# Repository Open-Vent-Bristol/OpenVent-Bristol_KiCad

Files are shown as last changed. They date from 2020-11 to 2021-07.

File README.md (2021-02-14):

OpenVent controller PCB, version A (KiCad) ported from version 2.7 (Altium,
incomplete), 2020-10-20, by Jeff Sutherland <jeffs@fomsystems.com>

All files for the Power Board are in the subfolder called "OV_Power". All control/main board files are in this folder level.
Electronic system diagram and overall device system diagram can be found here: https://docs.google.com/presentation/d/e/2PACX-1vRULcGT6Jc9GJDVb21LnrkGW9OiDjC7QJ2lRb0DsiA6KYFimniAMwYWqoMfq-0fJhvekxmhCl915fU4/pub?start=false&loop=true&delayms=3000&slide=id.gb10047446c_0_106
Also found by clicking "build" on https://openventbristol.co.uk/

Altium conversions aren't perfect but most everything is here.  Because the
schematic was incomplete and would not pass validation in Altium due to not
being complete a few things didn't make it across symbol-wise.  These will
have to be re-created in KiCad, but this is a trivial exercise.  Of more
import is the assigning of properties to all of the symbols in the schematics
so a sensible Bill of Materials may be generated directly from the schematic
or finished PCB layout.

All of the footprints that were currently in the Altium PCB came over and are
stored in the project footprint library.  These do not necessarily match the
schematic since the Altium PCB design reflects a former version of the
schematic as it had not been updated as yet.  So there is still much to do
before we can begin the process of creating the layout.  New mechanical
information is needed (see project documents).  The PCB layout for the former
version, stored for reference in the file "OpenVent_PCB-PcbDoc.kicad_pcb" does
not reflect the correct mechanical outline nor placement of components.  The
PCB footprints from the Altium design are missing information needed by KiCad
so if replacements are not available in the standard KiCad libraries then
these will have to be fixed.

TO DO's:
Complete schematic:
  a. Add BOM info to all symbols
  b. Complete circuit design
  c. Validate design

Process Board layout:
  a. load in missing footprints (use KiCad libraries, avoid creating
     footprints by hand if at all possible, if needed, fix existing ones.)
  b. Update PCB board outline, mech drill holes, and update placement and
     routing keepout areas
  c. Complete board placement and routing.
  d. Check association of footprints and 3D bodies; prepare STEP file of 3D
     image of board for mechanical group.

When creating symbols or updating fields in the schematic use the following
patterns for adding information to symbols in the lib or schemo:
   
   Field 0 is always 'Reference'
   Field 1 is always 'Value'
   Field 2 is always 'Footprint'
   Field 3 is always 'Datasheet'

These cannot be changed as they are required by the system.  The remaining
fields can be freely defined.  So in the case of OpenVent we need to
standardize how these are used to make sensible BOM generation possible.  For
example, something like this scheme could be used:

   Field 4 is defined as 'Val' (resistance, capacitance, inductance, etc.)
   Field 5 is defined as 'Voltage'
   Field 6 is defined as 'Tolerance'
   Field 7 is defined as 'Watt'  (usually just for resistors)
   Field 8 is defined as 'Current'  (usually for diodes and inductors)
   Field 9 is defined as 'Mfr' (manufacturer name)
   Field 10 is defined as 'Mfr_PN' (manufacturer's part number)
   Field 11 is defined as 'DistName' (this would be Farnell, DigiKey, etc.)
   Field 12 is defined as 'Dist_PN' (distributor's part number)
   Field 13 is defined as 'Detailed' (detailed description of part)

Optional fields can be added at will in the schematic to suit the needs of the
design or documentation efforts.

Notes on using KiCad:

  1. When setting up your KiCad installation you should also clone the
     repositories for the symbols, footprints and 3D models and refer to those
     in your 'manage libraries' settings rather than using the default
     libraries that came with your version of KiCad.  See github.com/kicad.

  2. Do not just add symbols to the design from the KiCad standard libraries.
     The symbols there are basically just "templates".  Copy standard symbols
     to a project library then add BOM and footprint info to the symbols if
     needed.

  3. Avoid creating your own footprints if at all possible.  Most every IC in
     common use already has a standard footprint in the KiCad libraries.

  4. All footprints should be kept in a local project library.  If
     modifications need to be made to paste or solder mask layers to deal with
     process issues copy footprints to another library and tag that library with
     the name of the PCB vendor so that managing artwork fudging among vendors can
     be easily sorted.

     After footprints are pulled into the PCB design from the standard KiCad
     libraries they may be exported to a local library to facilitate modifying any
     of their shapes to meet DFM requirements of a particular vendor.  Simply
     export the footprints to a project library from the PCB editor once the
     design has been transferred from the schematic and all the footprints
     have been accounted for.  There's no need to manually copy footprints
     from the KiCad libraries.

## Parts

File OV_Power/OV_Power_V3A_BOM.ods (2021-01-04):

Reference | Value | Footprint | Datasheet | Current | Desc | Detailed | DistName | Dist_PN | Mfr | Mfr_PN | Voltage | Tolerance | Val | Watt | Tol | Volt | DK_pn | Colour
Q2 | 2N7002BK | Package_TO_SOT_SMD:SOT-23 | https://assets.nexperia.com/documents/data-sheet/2N7002BK.pdf | 350mA | MOSFET N-CH 60V 350MA SOT23 | N-Channel 350mA (Ta) 370mW (Ta) Surface Mount TO-236AB | DigiKey | 1727-4789-2-ND | Nexperia USA Inc. | 2N7002BK,215 | 60V
C9 | 1uF_0603_Ceramic_Capacitor,_10%,_50V,_X5R | Capacitor_SMD:C_0603_1608Metric |  |  |  |  |  |  |  |  | 50V | 10% | 1uF
C1 | 100nF_0603_Ceramic_Capacitor,_10%,_X7R,_25V | Capacitor_SMD:C_0603_1608Metric |  |  |  |  |  |  |  |  | 25V | 10% | 100nF
U1 | LT3796 | F_ICs:TSSOP-28-LTvar_EB_4.4x9.7mm_P0.65mm | http://www.analog.com/media/en/technical-documentation/data-sheets/3796fb.pdf |  | IC LED DRIVER CTRLR DIM 28TSSOP | LED Driver IC 1 Output DC DC Controller SEPIC, Step-Down (Buck), Step-Up (Boost) Analog, PWM Dimming 28-TSSOP-EP |  |  | Analog Devices | LT3796IFE-1#TRPBF
L1 | MSD1260-333 | F_Inductors:MSD1260 | https://www.mouser.com/datasheet/2/597/msd1260-220355.pdf |  | Coupled Inductors 33uH | Coupled Inductors 33uH Shld 20% 2.32A 134mOhms | Mouser | 994-MSD1260-333MLB | Coilcraft | MSD1260-333MLB |  |  | 33uH
R10 | R_0805_050m_cursense | Resistor_SMD:R_0805_2012Metric | https://www.ohmite.com/assets/docs/res_kdv.pdf?r=false |  | RES 50M OHM 1% 1/4W 0805 | 50 mOhms ±1% 0.25W, 1/4W Chip Resistor 0805 (2012 Metric) Current Sense Metal Film | DigiKey | 273-KDV08FR050ETTR-ND | Ohmite | KDV08FR050ET |  | 1% | 0.05mOhm | 0.25W | 1.00%
Q1 | SSM3K341R | Package_TO_SOT_SMD:SOT-23 | https://toshiba.semicon-storage.com/info/docget.jsp?did=35714&prodName=SSM3K341R |  | MOSFET N-CH 60V 6A SOT-23F | N-Channel 60V 6A (Ta) 1.2W (Ta) Surface Mount SOT-23F | DigiKey | SSM3K341RLFTR-ND | Toshiba Semiconductor and Storage | SSM3K341R,LF
C6 | 2.2uF_2824_film_capacitor_10%_40V | F_Misc:CAPPC7360X380N | https://www.wima.de/wp-content/uploads/media/e_WIMA_SMD_PET.pdf |  | CAP FILM 2.2UF 10% 63VDC 2824 | 2.2µF Film Capacitor 40V 63V Polyester, Polyethylene Terephthalate (PET), Metallized 2824 (7260 Metric) |  |  | WIMA | SMDTC04220TB00KQ00 | 63V | 10% | 2.2uF
D3 | MBRS260T3G | Diode_SMD:D_SMB | https://www.onsemi.com/pub/Collateral/MBRS260T3-D.PDF | 2A | DIODE SCHOTTKY 60V 2A SMB | Diode Schottky 60V 2A Surface Mount SMB |  |  | ON Semiconductor | MBRS260T3G | 60V
R15 | R_1206_250m_cursense | Resistor_SMD:R_1206_3216Metric | https://www.yageo.com/upload/media/product/productsearch/datasheet/rchip/PYu-PT-Group_521_RoHS_L_2.pdf |  | RES 0.25 OHM 1% 1/2W 1206 | 250 mOhms ±1% 0.5W, 1/2W Chip Resistor 1206 (3216 Metric) Automotive AEC-Q200, Current Sense, Moisture Resistant Thick Film |  |  | Yageo | PT1206FR-7W0R25L |  | 1% | 250mOhm | 0.5W | 1.00%
R11 | R_0603_015m_cursense | Resistor_SMD:R_0603_1608Metric | https://www.ohmite.com/assets/docs/res_lvt.pdf?r=false |  | RES 0.015 OHM 1% 1/3W 0603 | 15 mOhms ±1% 0.333W, 1/3W Chip Resistor 0603 (1608 Metric) Current Sense Metal Element |  |  | Ohmite | LVT06R0150FER |  | 1% | 0.015mOhm | 1/3W | 1.00%
R9 | R_0603_2k_0.1W_1% | Resistor_SMD:R_0603_1608Metric |  |  |  |  |  |  |  |  |  | 1% | 2k | 0.1W
RT1 | R_Thermistor_0603_10K_NTC | Resistor_SMD:R_0603_1608Metric | https://www.vishay.com/docs/33008/nths.pdf |  | THERMISTOR NTC 10KOHM 3477K 0603 | NTC Thermistor 10k 0603 (1608 Metric) | DigiKey | 541-1107-2-ND | Vishay Dale | NTHS0603N02N1002JE |  | 5% | 10K
R17 | R_0603_30k1_0.1W_1% | Resistor_SMD:R_0603_1608Metric |  |  |  |  |  |  |  |  |  | 1% | 30k1 | 0.1W
R18 | R_0603_95k3_0.1W_1% | Resistor_SMD:R_0603_1608Metric |  |  |  |  |  |  |  |  |  | 1% | 95k3 | 0.1W
R19 | R_0603_10k2_0.1W_1% | Resistor_SMD:R_0603_1608Metric |  |  |  |  |  |  |  |  |  | 1% | 10k2 | 0.1W
R16 | R_0603_113k_0.1W_1% | Resistor_SMD:R_0603_1608Metric |  |  |  |  |  |  |  |  |  | 1% | 113k | 0.1W
R14 | R_0603_49k9_0.1W_1% | Resistor_SMD:R_0603_1608Metric |  |  |  |  |  |  |  |  |  | 1% | 49k9 | 0.1W
R6 | R_0603_499K_0.1W_1% | Resistor_SMD:R_0603_1608Metric |  |  |  |  |  |  |  |  |  | 1% | 499K | 0.1W
R7 | R_0603_97.6K_0.1W_1% | Resistor_SMD:R_0603_1608Metric |  |  |  |  |  |  |  |  |  | 1% | 97.6K | 0.1W
R1 | R_0603_806K_0.1W_1% | Resistor_SMD:R_0603_1608Metric |  |  |  |  |  |  |  |  |  | 1% | 806K | 0.1W
R2 | 20k_0603_Chip_Resistor,_1%,_0.1W | Resistor_SMD:R_0603_1608Metric |  |  |  |  |  |  |  |  |  | 1% | 20k | 1W
R5 | R_0603_19k6_0.1W_1% | Resistor_SMD:R_0603_1608Metric |  |  |  |  |  |  |  |  |  | 1% | 19k6 | 0.1W
R3 | R_0603_499R_0.1W_1% | Resistor_SMD:R_0603_1608Metric |  |  |  |  |  |  |  |  |  | 1% | 499 | 0.1W
C3 | 10nF_0603_Ceramic_Capacitor,_10%,_50V,_X7R- | Capacitor_SMD:C_0603_1608Metric |  |  |  |  |  |  |  |  | 50V | 10% | 10nF
R4 | R_0603_40k2K_0.1W_1% | Resistor_SMD:R_0603_1608Metric |  |  |  |  |  |  |  |  |  | 1% | 40k2 | 0.1W
C2 | 10nF_0603_Ceramic_Capacitor,_10%,_50V,_X7R- | Capacitor_SMD:C_0603_1608Metric |  |  |  |  |  |  |  |  | 50V | 10% | 10nF
C8 | C_1210_10uF_25V_10%_X7R | Capacitor_SMD:C_1210_3225Metric | http://www.samsungsem.com/kr/support/product-search/mlcc/CL32A106KAULNNE.jsp |  | CAP CER 10UF 25V X5R 1210 | 10µF ±10% 25V Ceramic Capacitor X5R 1210 (3225 Metric) |  |  | Samsung Electro-Mechanics | CL32A106KAULNNE | 25V | 10% | 10uF
U2 | LT1936 | F_ICs:LT_MS8E | https://www.analog.com/media/en/technical-documentation/data-sheets/1936fd.pdf |  | IC REG BUCK ADJ 1.4A 8MSOP | Buck Switching Regulator IC Positive Adjustable 1.2V 1 Output 1.4A 8-TSSOP, 8-MSOP (0.118 | 3.00mm Width) Exposed Pad" |  |  | Linear Technology | LT1936EMS8E#PBF
D1 | MBRS260T3G | Diode_SMD:D_SMB | https://www.onsemi.com/pub/Collateral/MBRS260T3-D.PDF | 2A | DIODE SCHOTTKY 60V 2A SMB | Diode Schottky 60V 2A Surface Mount SMB |  |  | ON Semiconductor | MBRS260T3G | 60V
C4 | 100nF_0603_Ceramic_Capacitor,_10%,_X7R,_25V | Capacitor_SMD:C_0603_1608Metric |  |  |  |  |  |  |  |  | 25V | 10% | 100nF
L2 | L_22uH_2.6A_42mOhm_SMT | F_Inductors:L-Bourns-SRU1048-series | https://www.bourns.com/docs/Product-Datasheets/SRU1048.pdf | 2.6A | FIXED IND 22UH 2.6A 42 MOHM SMD | 22µH Shielded Wirewound Inductor 2.6A 42mOhm Nonstandard with Ferrite core |  |  | Bourns Inc. | SRU1048-220Y |  |  | 22uH
C5 | C_0603_0.22uf_25V_10% | Capacitor_SMD:C_0603_1608Metric | https://search.murata.co.jp/Ceramy/image/img/A01X/G101/ENG/GCM188R71E224KA55-01.pdf |  | CAP CER 0.22UF 25V X7R 0603 | 0.22µF ±10% 25V Ceramic Capacitor X7R 0603 (1608 Metric) |  |  | Murata Electronics | GCM188R71E224KA55J | 25V | 10% | 0.22uF |  | 10% | 25V
R12 | R_0603_53K_0.1W_1% | Resistor_SMD:R_0603_1608Metric | https://www.digikey.com/en/products/result |  | RES 53K OHM 1% 1/10W 0603 | 53 kOhms ±1% 0.1W, 1/10W Chip Resistor 0603 (1608 Metric) Automotive AEC-Q200, Moisture Resistant Metal Film |  |  | KOA Speer Electronics, Inc. | RN73H1JTTD5302F25 |  | 1% | 53k | 0.1W | 1%
D2 | MMBD914 | Package_TO_SOT_SMD:SOT-23 | https://www.vishay.com/docs/85734/mmbd914.pdf | 200mA | DIODE GEN PURP 100V 200MA SOT23 | Diode Standard 100V 200mA Surface Mount SOT-23 |  |  | Vishay Semiconductor Diodes Division | MMBD914-E3-08 | 100V |  |  |  |  | 100V
R13 | 10k_0603_Chip_Resistor,_1%,_0.1W | Capacitor_SMD:C_0603_1608Metric | ~ |  |  |  |  |  |  |  |  | 1% | 10k | 0.1W
C7 | 10uF_0805_Ceramic_Capacitor_10%_X7R_10V | Capacitor_SMD:C_0805_2012Metric | https://search.murata.co.jp/Ceramy/image/img/A01X/G101/ENG/GCM21BR71A106KE22-01.pdf |  | CAP CER 10UF 10V X7R 0805 | Ceramic Capacitor | DigiKey | 490-10674-2-ND | Murata Electronics | GCM21BR71A106KE22L | 10V | 10% | 10uF
R8 | 100K_0603_Chip_Resistor,_1%,_0.1W | Resistor_SMD:R_0603_1608Metric |  |  |  |  |  |  |  |  |  | 1% | 100k | 0.1W
C14 | 100nF_0603_Ceramic_Capacitor,_10%,_X7R,_25V | Capacitor_SMD:C_0603_1608Metric |  |  |  |  |  |  |  |  | 25V | 10% | 100nF
J4 | SpadeLug | F_Connectors:TE_1217861-1 | https://www.te.com/commerce/DocumentDelivery/DDEController?Action=srchrtrv&DocNm=1217861&DocType=Customer+Drawing&DocLang=English |  | CONN QC TAB 0.250 SOLDER | 0.250" (6.35mm) Quick Connect Male Solder Connector Non-Insulated |  |  | TE Connectivity AMP Connectors | 1217861-1 |  |  |  |  |  |  | A100452CT-ND
J5 | SpadeLug | F_Connectors:TE_1217861-1 | https://www.te.com/commerce/DocumentDelivery/DDEController?Action=srchrtrv&DocNm=1217861&DocType=Customer+Drawing&DocLang=English |  | CONN QC TAB 0.250 SOLDER | 0.250" (6.35mm) Quick Connect Male Solder Connector Non-Insulated |  |  | TE Connectivity AMP Connectors | 1217861-1 |  |  |  |  |  |  | A100452CT-ND
F1 | Polyfuse_10A | OpenVent:LF_16R1000G | https://www.littelfuse.com/~/media/electronics/datasheets/resettable_ptcs/littelfuse_ptc_16r_datasheet.pdf.pdf | 10A | PTC RESET FUSE 16V 10A RADIAL | Polymeric PTC Resettable Fuse 16V 10A Ih Through Hole Radial, Disc |  |  | Littelfuse Inc. | 16R1000GMR | 16V
D4 | S1B | Diode_SMD:D_SMA | https://www.onsemi.com/pub/Collateral/S1M-D.pdf | 1A | DIODE GEN PURP 100V 1A SMA | Diode Standard 100V 1A Surface Mount SMA (DO-214AC) |  |  | ON Semiconductor | S1B | 100V
C15 | 100nF_0603_Ceramic_Capacitor,_10%,_X7R,_25V | Capacitor_SMD:C_0603_1608Metric |  |  |  |  |  |  |  |  | 25V | 10% | 100nF
R24 | 1K_0603_Chip_Resistor,_1%,_0.1W | Resistor_SMD:R_0603_1608Metric |  |  |  |  |  |  |  |  |  | 1% | 1K | 0.1W
CN1 | CONN_HEADER_R_A_2POS_2.5MM | OpenVent:53426-0210 | https://www.molex.com/pdm_docs/sd/534260210_sd.pdf |  |  |  |  |  | Molex | 534260210
U4 | VNH5019ATR-E | Package_SO:ST_MultiPowerSO-30 | http://www.st.com/content/ccc/resource/technical/document/datasheet/1c/26/60/a8/3e/70/4c/e1/CD00234623.pdf/files/CD00234623.pdf/jcr:content/translations/en.CD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 |  | IC MTR DRV 5.5-24V MULTIPWRSO-30 | Motor Driver Power MOSFET Parallel, PWM MultiPowerSO-30 | DigiKey | 497-13073-2-ND | STMicroelectronics | VNH5019ATR-E
R25 | 1K_0603_Chip_Resistor,_1%,_0.1W | Resistor_SMD:R_0603_1608Metric |  |  |  |  |  |  |  |  |  | 1% | 1K
R26 | 1K_0603_Chip_Resistor,_1%,_0.1W | Resistor_SMD:R_0603_1608Metric |  |  |  |  |  |  |  |  |  | 1% | 1K
D6 | LED_Red_0603_SMD | LED_SMD:LED_0603_1608Metric | http://optoelectronics.liteon.com/upload/download/DS22-2005-077/LTST-C193KRKT-5A.PDF |  | LED RED CLEAR CHIP SMD | Red 631nm LED Indication - Discrete 2V 0603 (1608 Metric) | DigiKey | 160-1830-2-ND | Lite-On Inc. | LTST-C193KRKT-5A |  |  |  |  |  |  |  | RED
D5 | LED_GREEN_0603_SMD | LED_SMD:LED_0603_1608Metric | https://www.rohm.com/datasheet/SML-D12M8W(C)/sml-d12x8(c)-e |  | LED YELLOW/GREEN 1608 SMD | Yellow-Green 572nm LED Indication - Discrete 2.2V 0603 (1608 Metric) | DigiKey | SML-D12M8WT86CTR-ND | Rohm Semiconductor | SML-D12M8WT86C |  |  |  |  |  |  |  | GREEN
R31 | 1K_0603_Chip_Resistor,_1%,_0.1W | Resistor_SMD:R_0603_1608Metric |  |  |  |  |  |  |  |  |  | 1% | 1K
C11 | 1000uF_25V_Aluminium_SMD_Capacitor,_20% | Capacitor_SMD:CP_Elec_10x10 | https://www.digikey.com/en/product-highlight/u/united-chemi-con/mzs-series-aluminum-electrolytic-capacitors |  | CAP ALUM 1000UF 20% 25V SMD | Aluminum Electrolytic Capacitors Radial, Can - SMD 60mOhm @ 100kHz 2000 Hrs @ 105°C | DigiKey | 565-5120-2-ND | United Chemi-Con | EMZS250ARA102MJA0G | 25V | 20% | 1000uF
R23 | 1K_0603_Chip_Resistor,_1%,_0.1W | Resistor_SMD:R_0603_1608Metric |  |  |  |  |  |  |  |  |  | 1% | 1K
C12 | 1000uF_25V_Aluminium_SMD_Capacitor,_20% | Capacitor_SMD:CP_Elec_10x10 | https://www.digikey.com/en/product-highlight/u/united-chemi-con/mzs-series-aluminum-electrolytic-capacitors |  | CAP ALUM 1000UF 20% 25V SMD | Aluminum Electrolytic Capacitors Radial, Can - SMD 60mOhm @ 100kHz 2000 Hrs @ 105°C | DigiKey | 565-5120-2-ND | United Chemi-Con | EMZS250ARA102MJA0G | 25V | 20% | 1000uF
U3 | LT6106 | Package_TO_SOT_SMD:TSOT-23-5 | https://www.analog.com/media/en/technical-documentation/data-sheets/6106fb.pdf |  | IC CURR SENSE 1 CIRCUIT TSOT23-5 | Current Sense Amplifier 1 Circuit TSOT-23-5 |  |  | Analog Devices Inc. | LT6106IS5#TRPBF
R20 | R_0603_100_0.1W_0.1% | Resistor_SMD:R_0603_1608Metric | https://www.yageo.com/upload/media/product/productsearch/datasheet/rchip/PYu-RT_1-to-0.01_RoHS_L_12.pdf |  | RES SMD 100 OHM 0.1% 1/10W 0603 | 100 Ohms ±0.1% 0.1W, 1/10W Chip Resistor 0603 (1608 Metric) Thin Film |  |  | Yageo | RT0603BRD07100RL |  | 0.1% | 100 | 0.1W
R22 | R_0603_2k74_0.1W_0.1% | Resistor_SMD:R_0603_1608Metric | https://www.yageo.com/upload/media/product/productsearch/datasheet/rchip/PYu-RT_1-to-0.01_RoHS_L_12.pdf |  | RES SMD 2.74KOHM 0.1% 1/10W 0603 | 2.74 kOhms ±0.1% 0.1W, 1/10W Chip Resistor 0603 (1608 Metric) Thin Film |  |  | Yageo | RT0603BRE072K74L |  | 0.1% | 2k74 | 0.1W
R21 | R_2512_15m_cursense | Resistor_SMD:R_2512_6332Metric | https://riedon.com/media/pdf/CSR.pdf |  | RES 0.015 OHM 1% 2W 2512 | 15 mOhms ±1% 2W Chip Resistor 2512 (6432 Metric) Current Sense, Non-Inductive Metal Element |  |  | Riedon | CSR2512A0R015F |  | 1% | 15mOhm | 2W | 1.00%
C10 | 100nF_0603_Ceramic_Capacitor,_10%,_X7R,_25V | Capacitor_SMD:C_0603_1608Metric |  |  |  |  |  |  |  |  | 25V | 10% | 100nF
C16 | 1000uF_25V_Aluminium_SMD_Capacitor,_20% | Capacitor_SMD:CP_Elec_10x10 | https://www.digikey.com/en/product-highlight/u/united-chemi-con/mzs-series-aluminum-electrolytic-capacitors |  | CAP ALUM 1000UF 20% 25V SMD | Aluminum Electrolytic Capacitors Radial, Can - SMD 60mOhm @ 100kHz 2000 Hrs @ 105°C | DigiKey | 565-5120-2-ND | United Chemi-Con | EMZS250ARA102MJA0G | 25V | 20% | 1000uF
C17 | 1000uF_25V_Aluminium_SMD_Capacitor,_20% | Capacitor_SMD:CP_Elec_10x10 | https://www.digikey.com/en/product-highlight/u/united-chemi-con/mzs-series-aluminum-electrolytic-capacitors |  | CAP ALUM 1000UF 20% 25V SMD | Aluminum Electrolytic Capacitors Radial, Can - SMD 60mOhm @ 100kHz 2000 Hrs @ 105°C | DigiKey | 565-5120-2-ND | United Chemi-Con | EMZS250ARA102MJA0G | 25V | 20% | 1000uF
C18 | 1000uF_25V_Aluminium_SMD_Capacitor,_20% | Capacitor_SMD:CP_Elec_10x10 | https://www.digikey.com/en/product-highlight/u/united-chemi-con/mzs-series-aluminum-electrolytic-capacitors |  | CAP ALUM 1000UF 20% 25V SMD | Aluminum Electrolytic Capacitors Radial, Can - SMD 60mOhm @ 100kHz 2000 Hrs @ 105°C | DigiKey | 565-5120-2-ND | United Chemi-Con | EMZS250ARA102MJA0G | 25V | 20% | 1000uF
C19 | 1000uF_25V_Aluminium_SMD_Capacitor,_20% | Capacitor_SMD:CP_Elec_10x10 | https://www.digikey.com/en/product-highlight/u/united-chemi-con/mzs-series-aluminum-electrolytic-capacitors |  | CAP ALUM 1000UF 20% 25V SMD | Aluminum Electrolytic Capacitors Radial, Can - SMD 60mOhm @ 100kHz 2000 Hrs @ 105°C | DigiKey | 565-5120-2-ND | United Chemi-Con | EMZS250ARA102MJA0G | 25V | 20% | 1000uF
U7 | LTC4416 | Package_SO:MSOP-10_3x3mm_P0.5mm | http://www.linear.com/docs/17899 |  | IC OR CTRLR SRC SELECT 10MSOP | OR Controller Source Selector Switch P-Channel 2:2 10-MSOP |  |  | Analog Devices / Linear Technology | LTC4416IMS#TRPBF
U8 | AOSD21307 | Package_SO:SOIC-8_3.9x4.9mm_P1.27mm | www.aosmd.com/res/data_sheets/AOSD21307.pdf |  | 30V DUAL P-CHANNEL MOSFET | Mosfet Array 2 P-Channel (Dual) 30V 9A (Ta) 2W (Ta) Surface Mount 8-SOIC |  |  | Alpha & Omega Semiconductor Inc. | AOSD21307
U9 | AOSD21307 | Package_SO:SOIC-8_3.9x4.9mm_P1.27mm | www.aosmd.com/res/data_sheets/AOSD21307.pdf |  | 30V DUAL P-CHANNEL MOSFET | Mosfet Array 2 P-Channel (Dual) 30V 9A (Ta) 2W (Ta) Surface Mount 8-SOIC |  |  | Alpha & Omega Semiconductor Inc. | AOSD21307
R39 | 10k_0603_Chip_Resistor,_1%,_0.1W | Resistor_SMD:R_0603_1608Metric |  |  |  |  |  |  |  |  |  | 1% | 10k | 0.1W
R37 | R_0603_24k9_0.1W_1% | Resistor_SMD:R_0603_1608Metric |  |  |  |  |  |  |  |  |  | 1% | 24k9 | 0.1W
R38 | R_0603_221K_0.1W_1% | Resistor_SMD:R_0603_1608Metric |  |  |  |  |  |  |  |  |  | 1% | 221K | 0.1W
R36 | R_0603_178K_0.1W_1% | Resistor_SMD:R_0603_1608Metric |  |  |  |  |  |  |  |  |  | 1% | 178K | 0.1W
C13 | C_1210_10uF_25V_10%_X7R | Capacitor_SMD:C_1210_3225Metric | http://www.samsungsem.com/kr/support/product-search/mlcc/CL32A106KAULNNE.jsp |  | CAP CER 10UF 25V X5R 1210 | 10µF ±10% 25V Ceramic Capacitor X5R 1210 (3225 Metric) |  |  | Samsung Electro-Mechanics | CL32A106KAULNNE | 25V | 10% | 10uF
J2 | Conn_HDR_2x10_latching | F_Misc:3M_D3428-6302-AR | https://multimedia.3m.com/mws/media/485761O/3mtm-four-wall-header-ts2245.pdf |  | CONN HEADER VERT 20POS 2.54MM LATCHING | Connector Header Through Hole 20 position 0.100" (2.54mm) with latches |  |  | 3M | D3428-6302-AR
J1 | Kycon_kpjx-4s_shielded | OpenVent:Kycon_KPJX-4S_SHIELD | http://www.kycon.com/Pub_Eng_Draw/KPJX-4S-S.pdf |  | CONN JACK FMALE 4POS TIN SOLDER | 4 (Power) Position Circular Connector Jack, Female Sockets Solder |  |  | Kycon, Inc. | KPJX-4S-S
J3 | 532530670 | Connector_Molex:Molex_Micro-Latch_53253-0670_1x06_P2.00mm_Vertical | https://www.molex.com/pdm_docs/sd/532530270_sd.pdf |  | CONN HEADER VERT 6POS 2MM | Connector Header Through Hole 6 position 0.079" (2.00mm) |  |  | Molex | 532530670
J6 | CONN_HEADER_2.54X2_MOLEX_KK_Series | Connector_Molex:Molex_KK-254_AE-6410-02A_1x02_P2.54mm_Vertical | https://www.molex.com/webdocs/datasheets/pdf/en-us//0022232021_PCB_HEADERS.pdf |  | CONN HEADER VERT 2POS 2.54MM | Connector Header Through Hole 2 position 0.100" (2.54mm) |  |  | Molex | 22232021
J7 | CONN_HEADER_2.54X2_MOLEX_KK_Series | Connector_Molex:Molex_KK-254_AE-6410-02A_1x02_P2.54mm_Vertical | https://www.molex.com/webdocs/datasheets/pdf/en-us//0022232021_PCB_HEADERS.pdf |  | CONN HEADER VERT 2POS 2.54MM | Connector Header Through Hole 2 position 0.100" (2.54mm) |  |  | Molex | 22232021
Q4 | SZNUD3124LT1G | Package_TO_SOT_SMD:SOT-23 | http://www.onsemi.com/pub/Collateral/NUD3124-D.PDF | 150mA | IC PWR DRVR N-CHAN 1:1 SOT23-3 | Power Switch/Driver 1:1 N-Channel 150mA SOT-23-3 (TO-236) |  |  | ON Semiconductor | SZNUD3124LT1G | 12V
Q3 | SZNUD3124LT1G | Package_TO_SOT_SMD:SOT-23 | http://www.onsemi.com/pub/Collateral/NUD3124-D.PDF | 150mA | IC PWR DRVR N-CHAN 1:1 SOT23-3 | Power Switch/Driver 1:1 N-Channel 150mA SOT-23-3 (TO-236) |  |  | ON Semiconductor | SZNUD3124LT1G | 12V
R27 | 1K_0603_Chip_Resistor,_1%,_0.1W | Resistor_SMD:R_0603_1608Metric |  |  |  |  |  |  |  |  |  | 1% | 1K | 0.1W

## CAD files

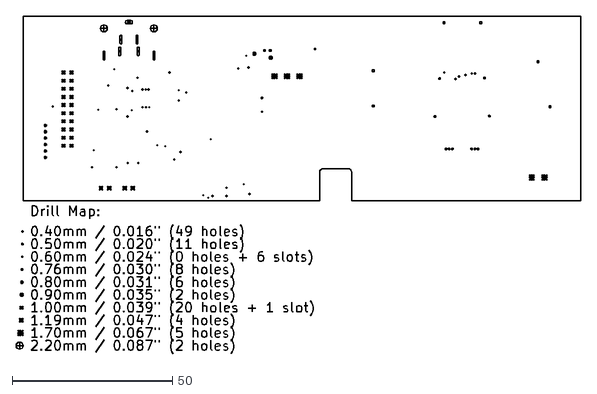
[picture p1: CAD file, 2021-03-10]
OV_Power/plots/OV_Power-PTH-drl_map.dxf
176.2 x 105.3

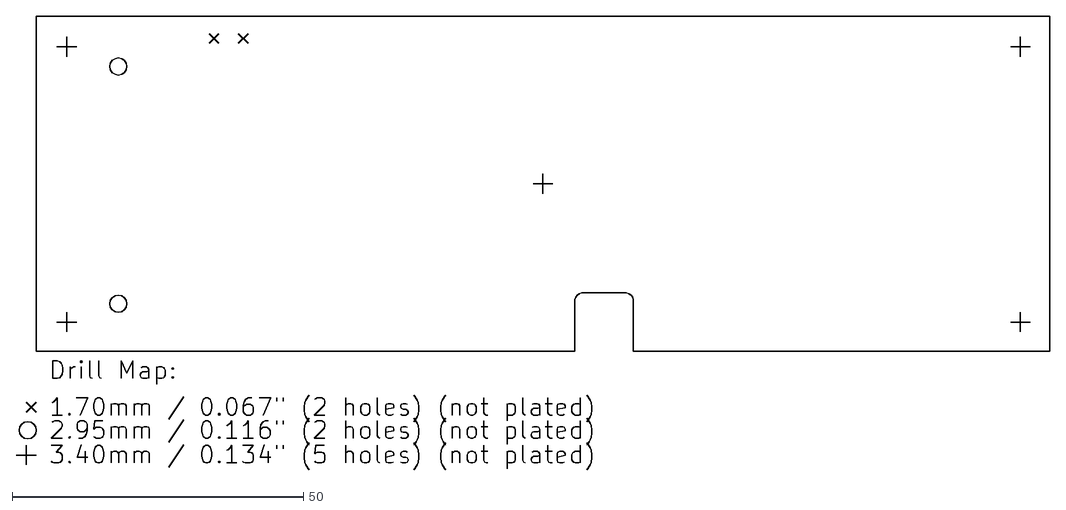
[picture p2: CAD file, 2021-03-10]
OV_Power/plots/OV_Power-NPTH-drl_map.dxf
177.4 x 77.8

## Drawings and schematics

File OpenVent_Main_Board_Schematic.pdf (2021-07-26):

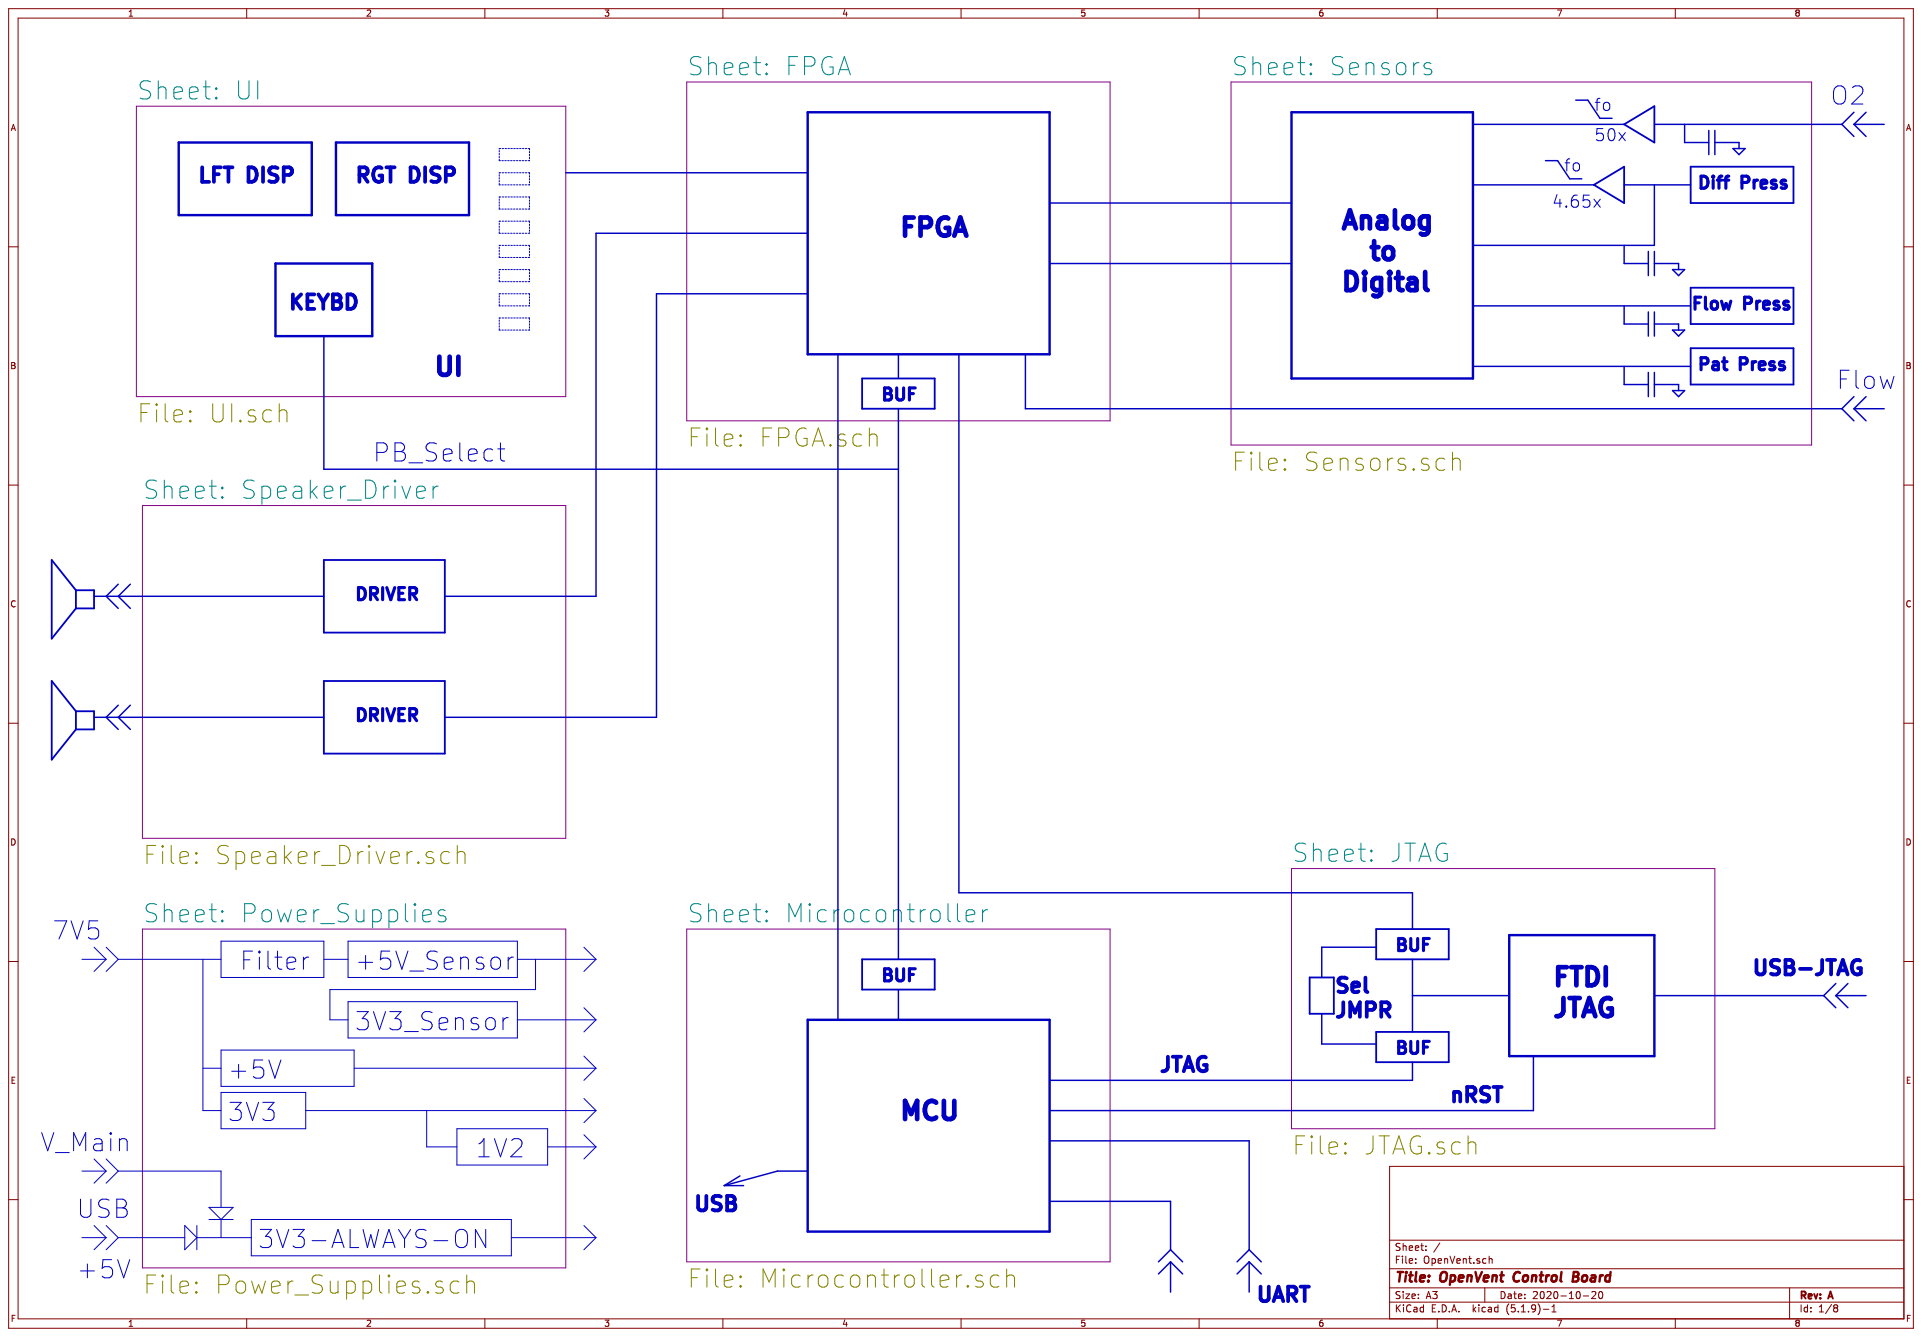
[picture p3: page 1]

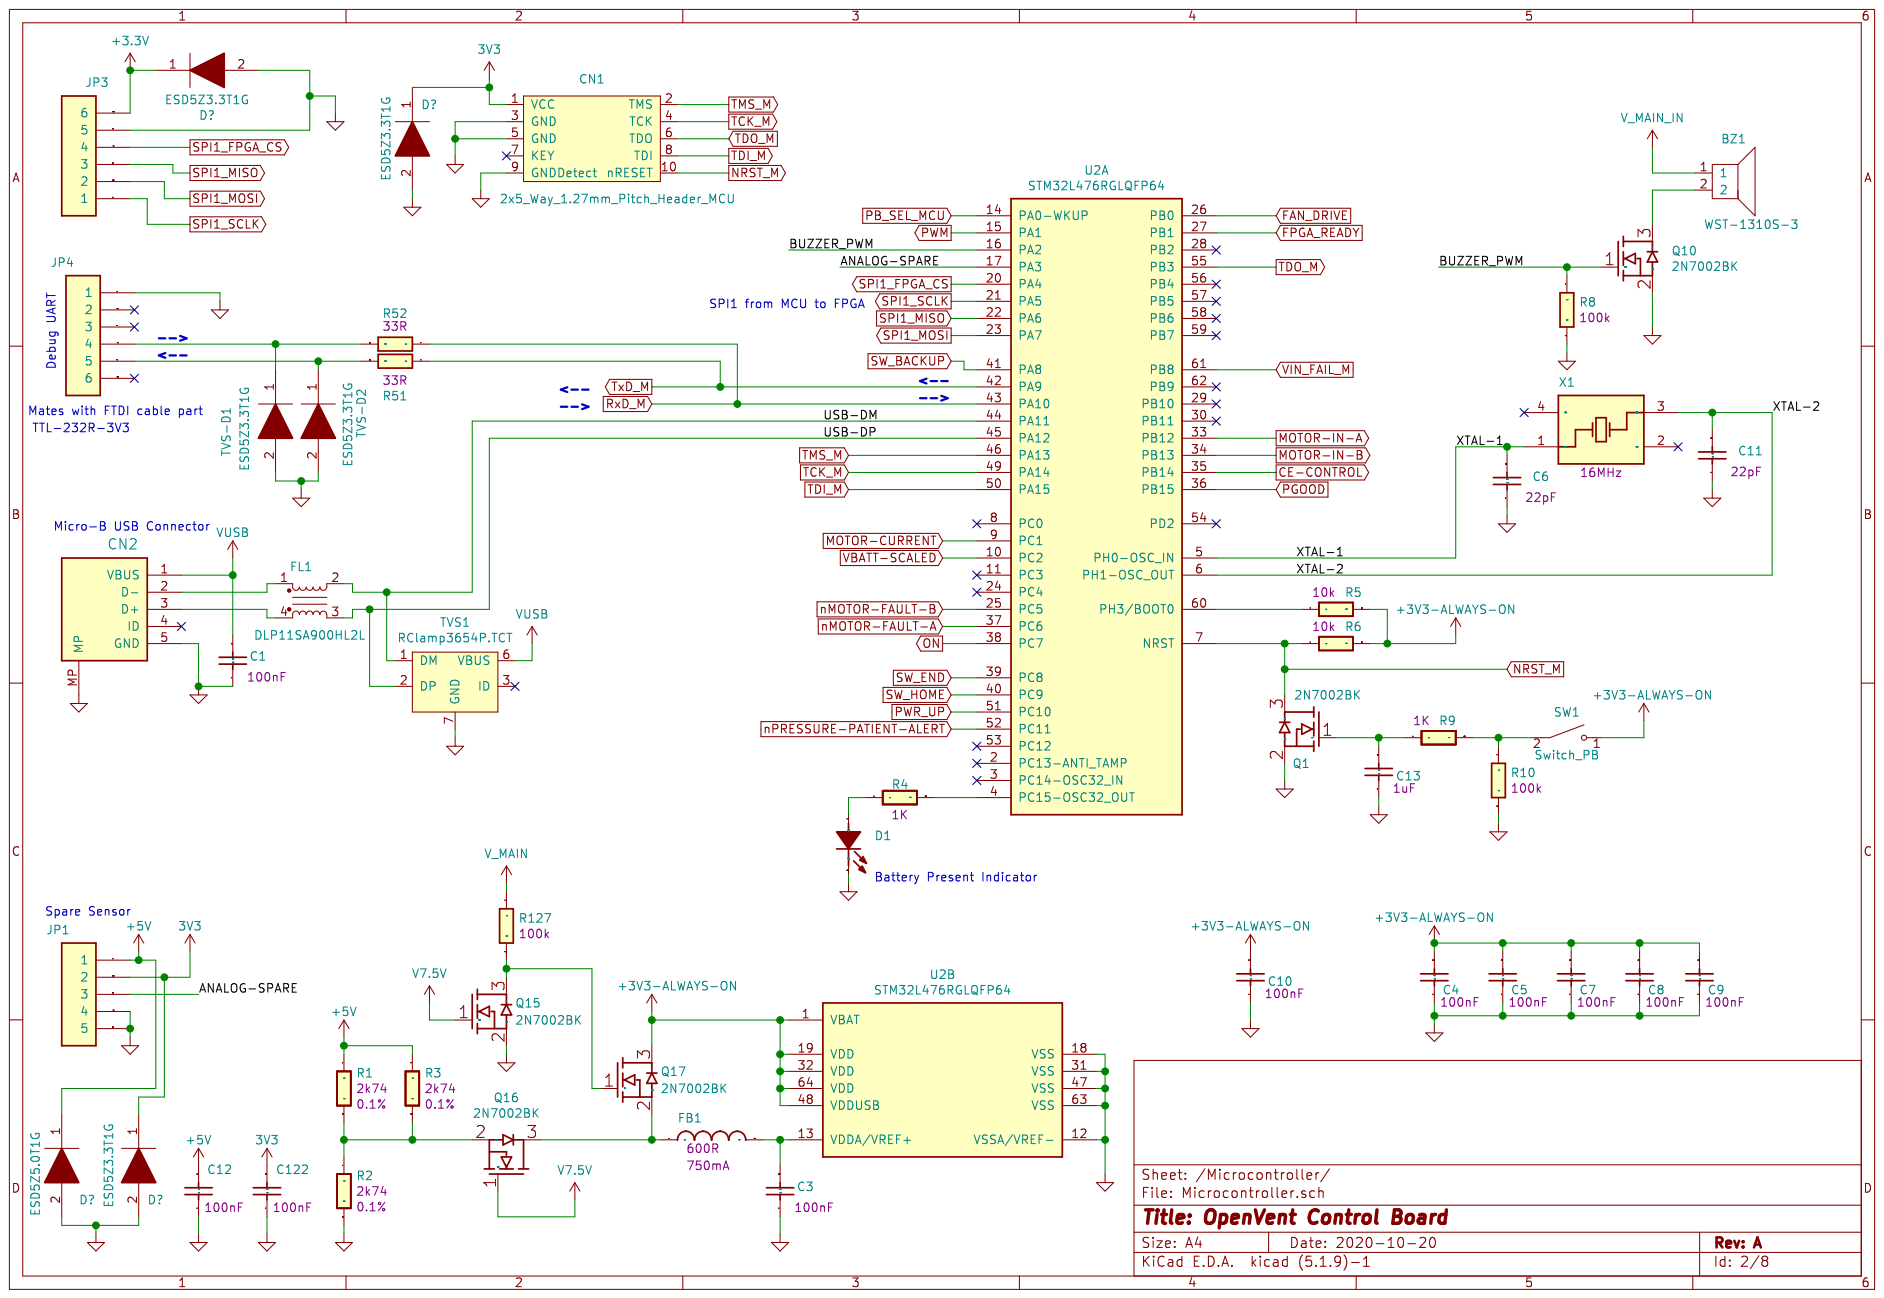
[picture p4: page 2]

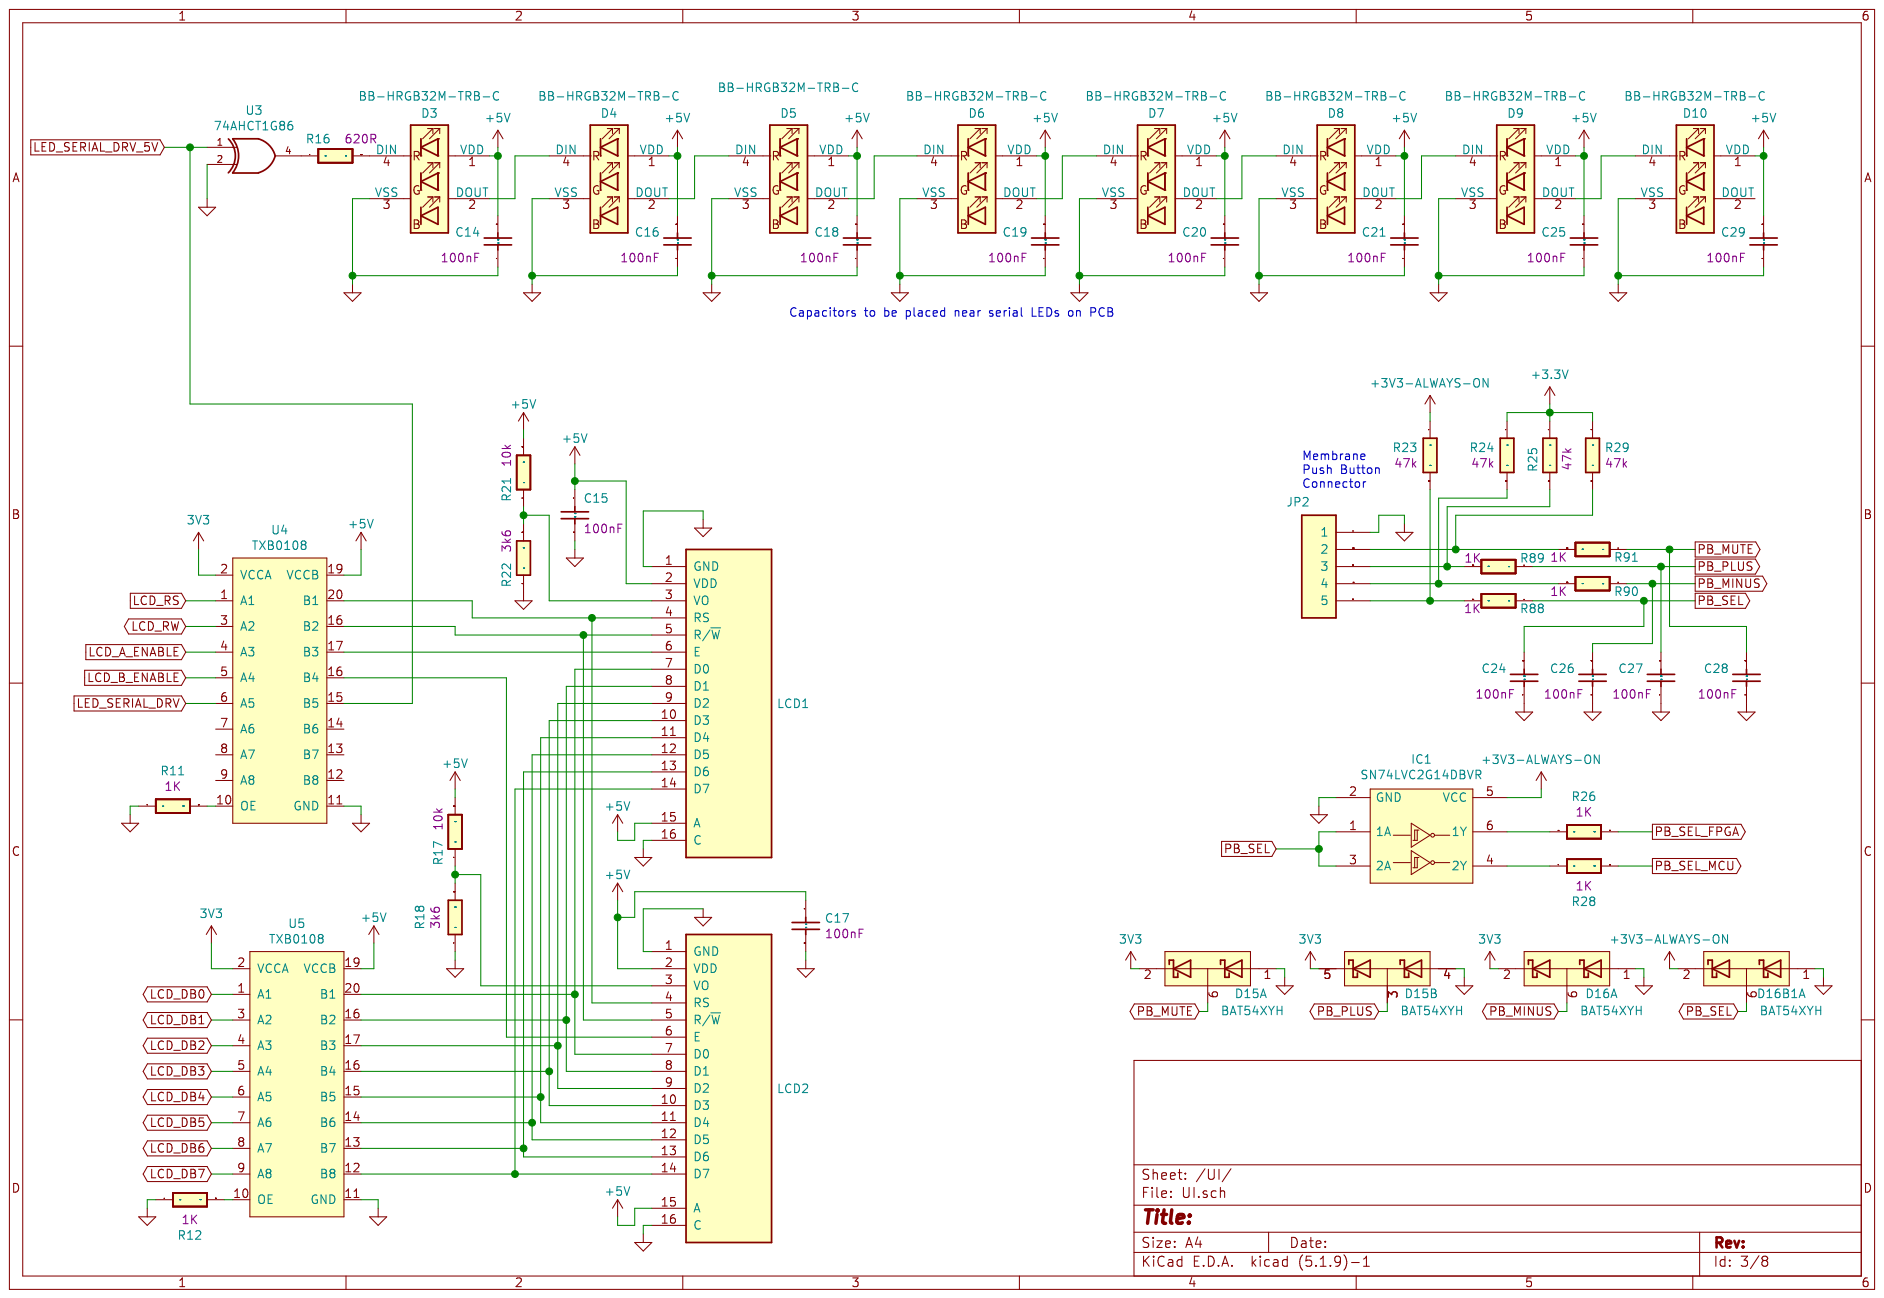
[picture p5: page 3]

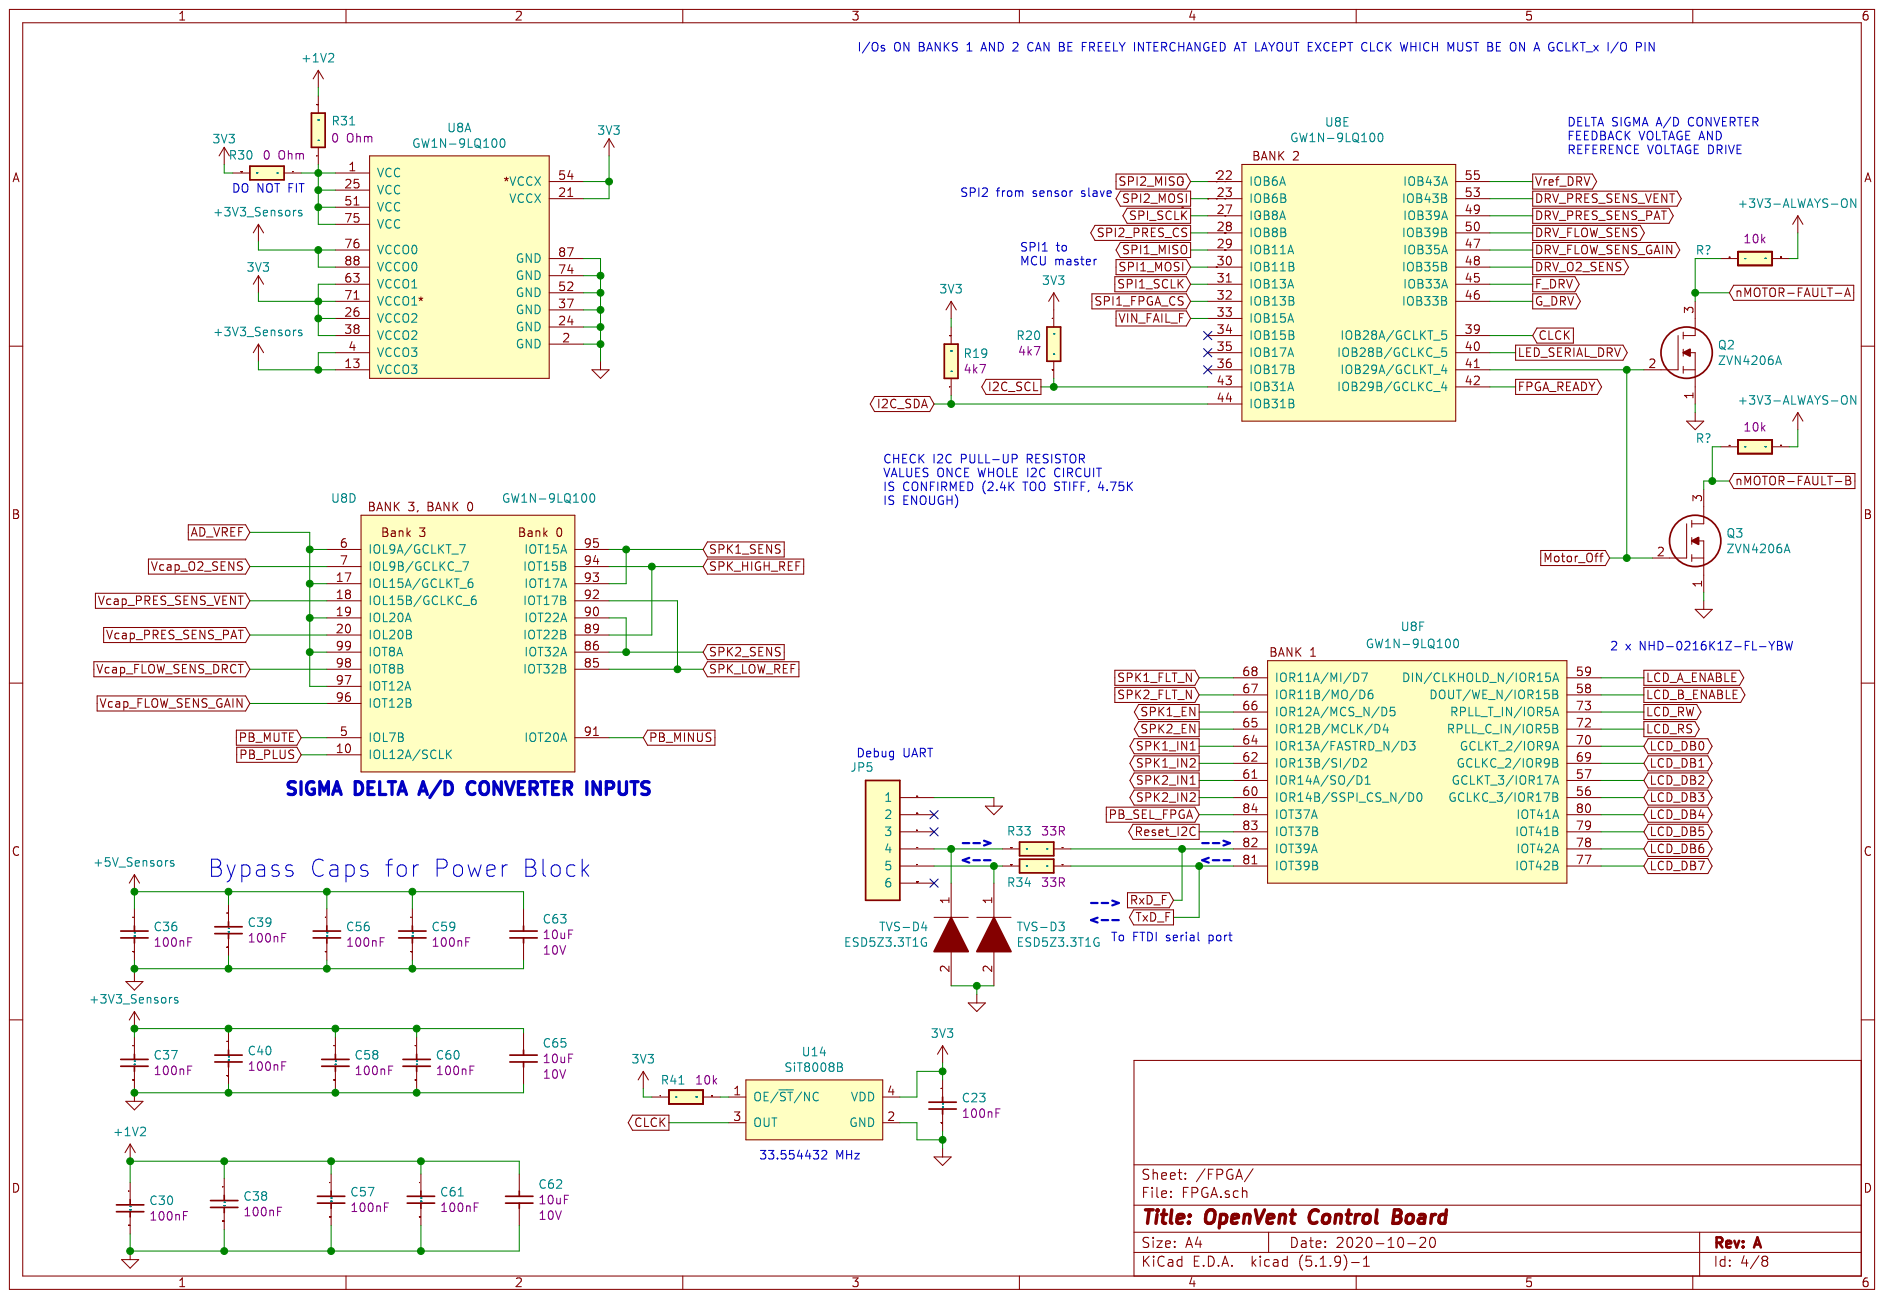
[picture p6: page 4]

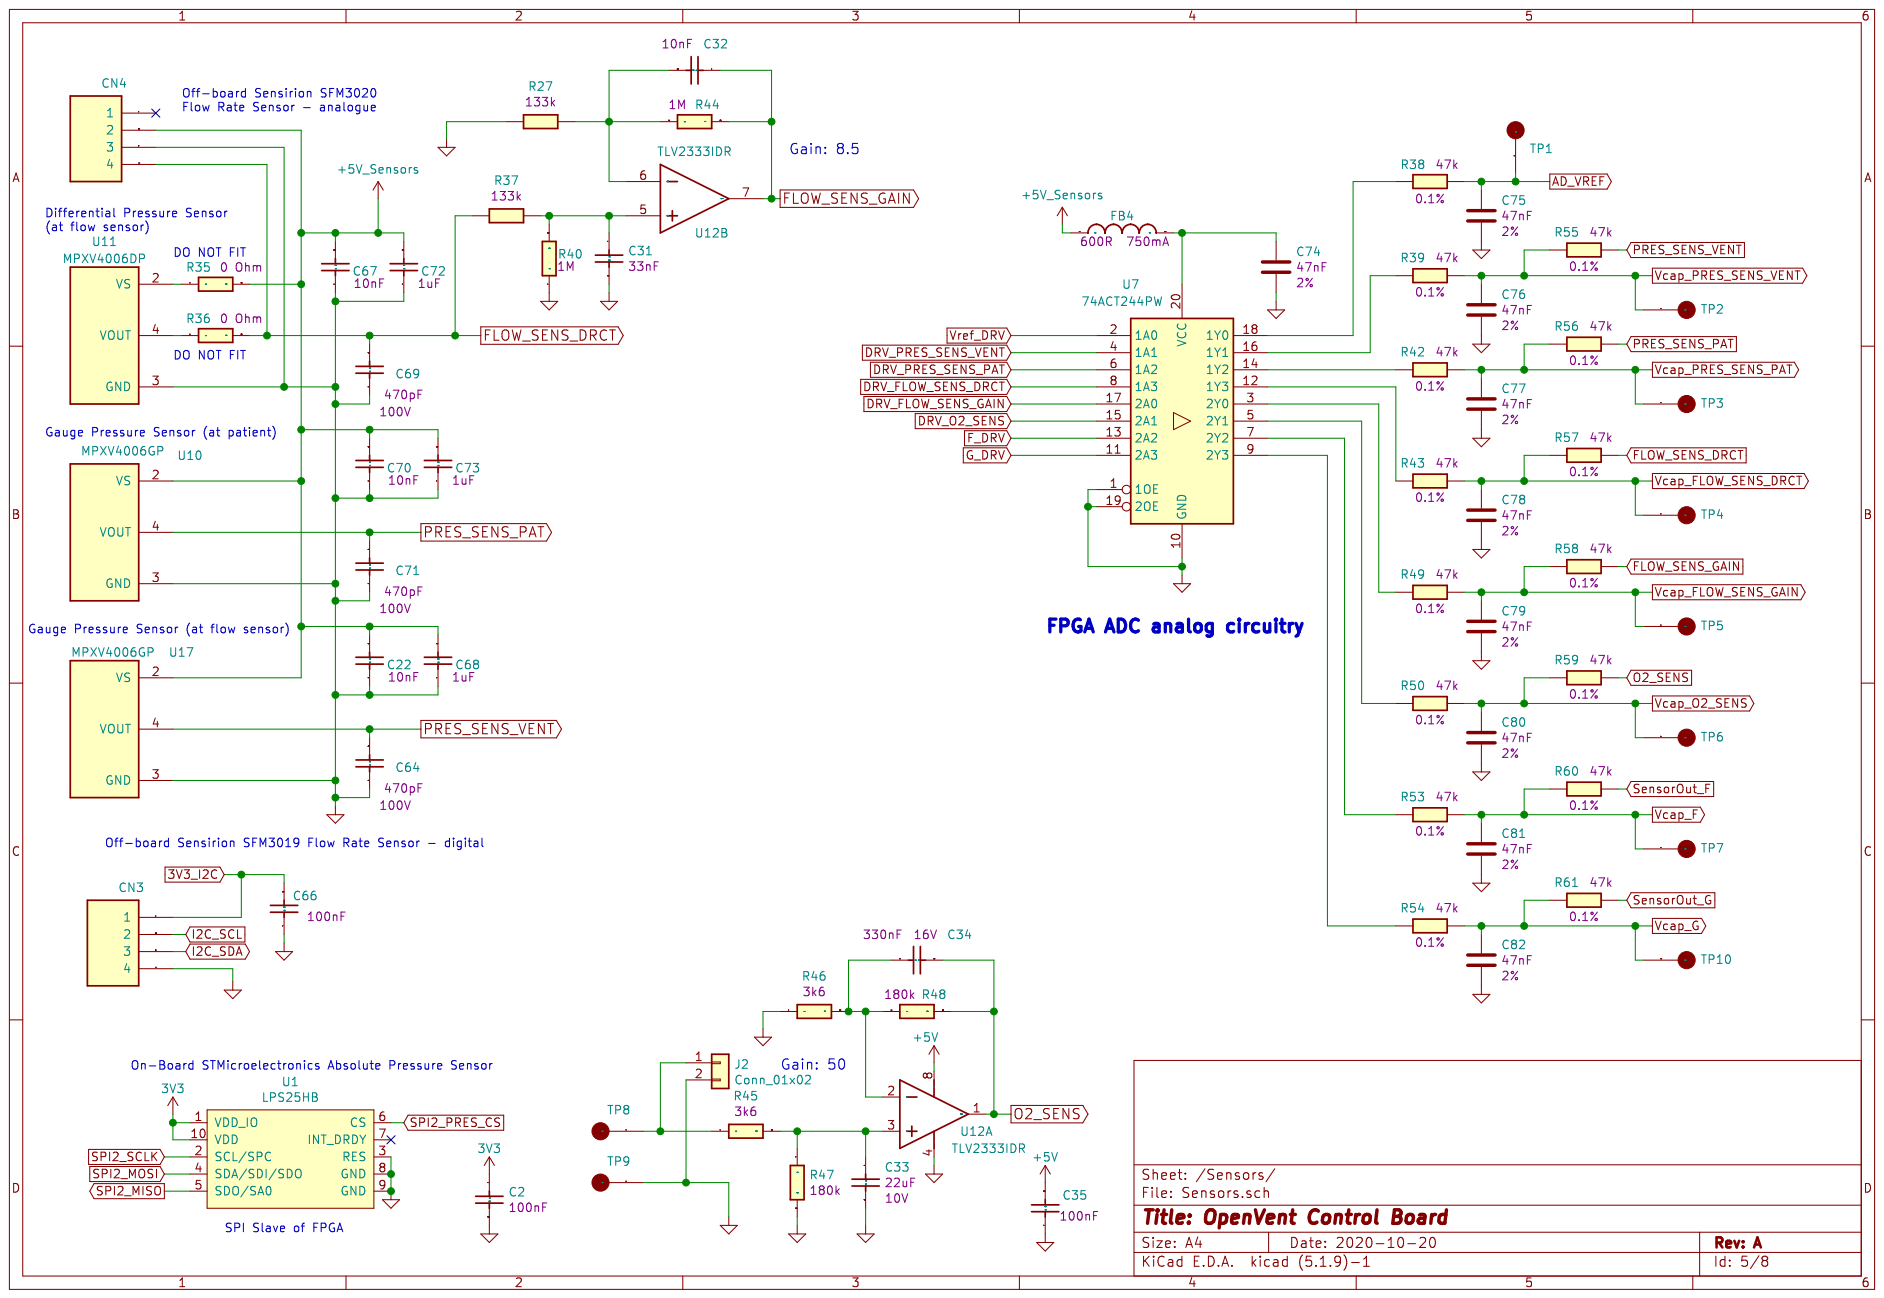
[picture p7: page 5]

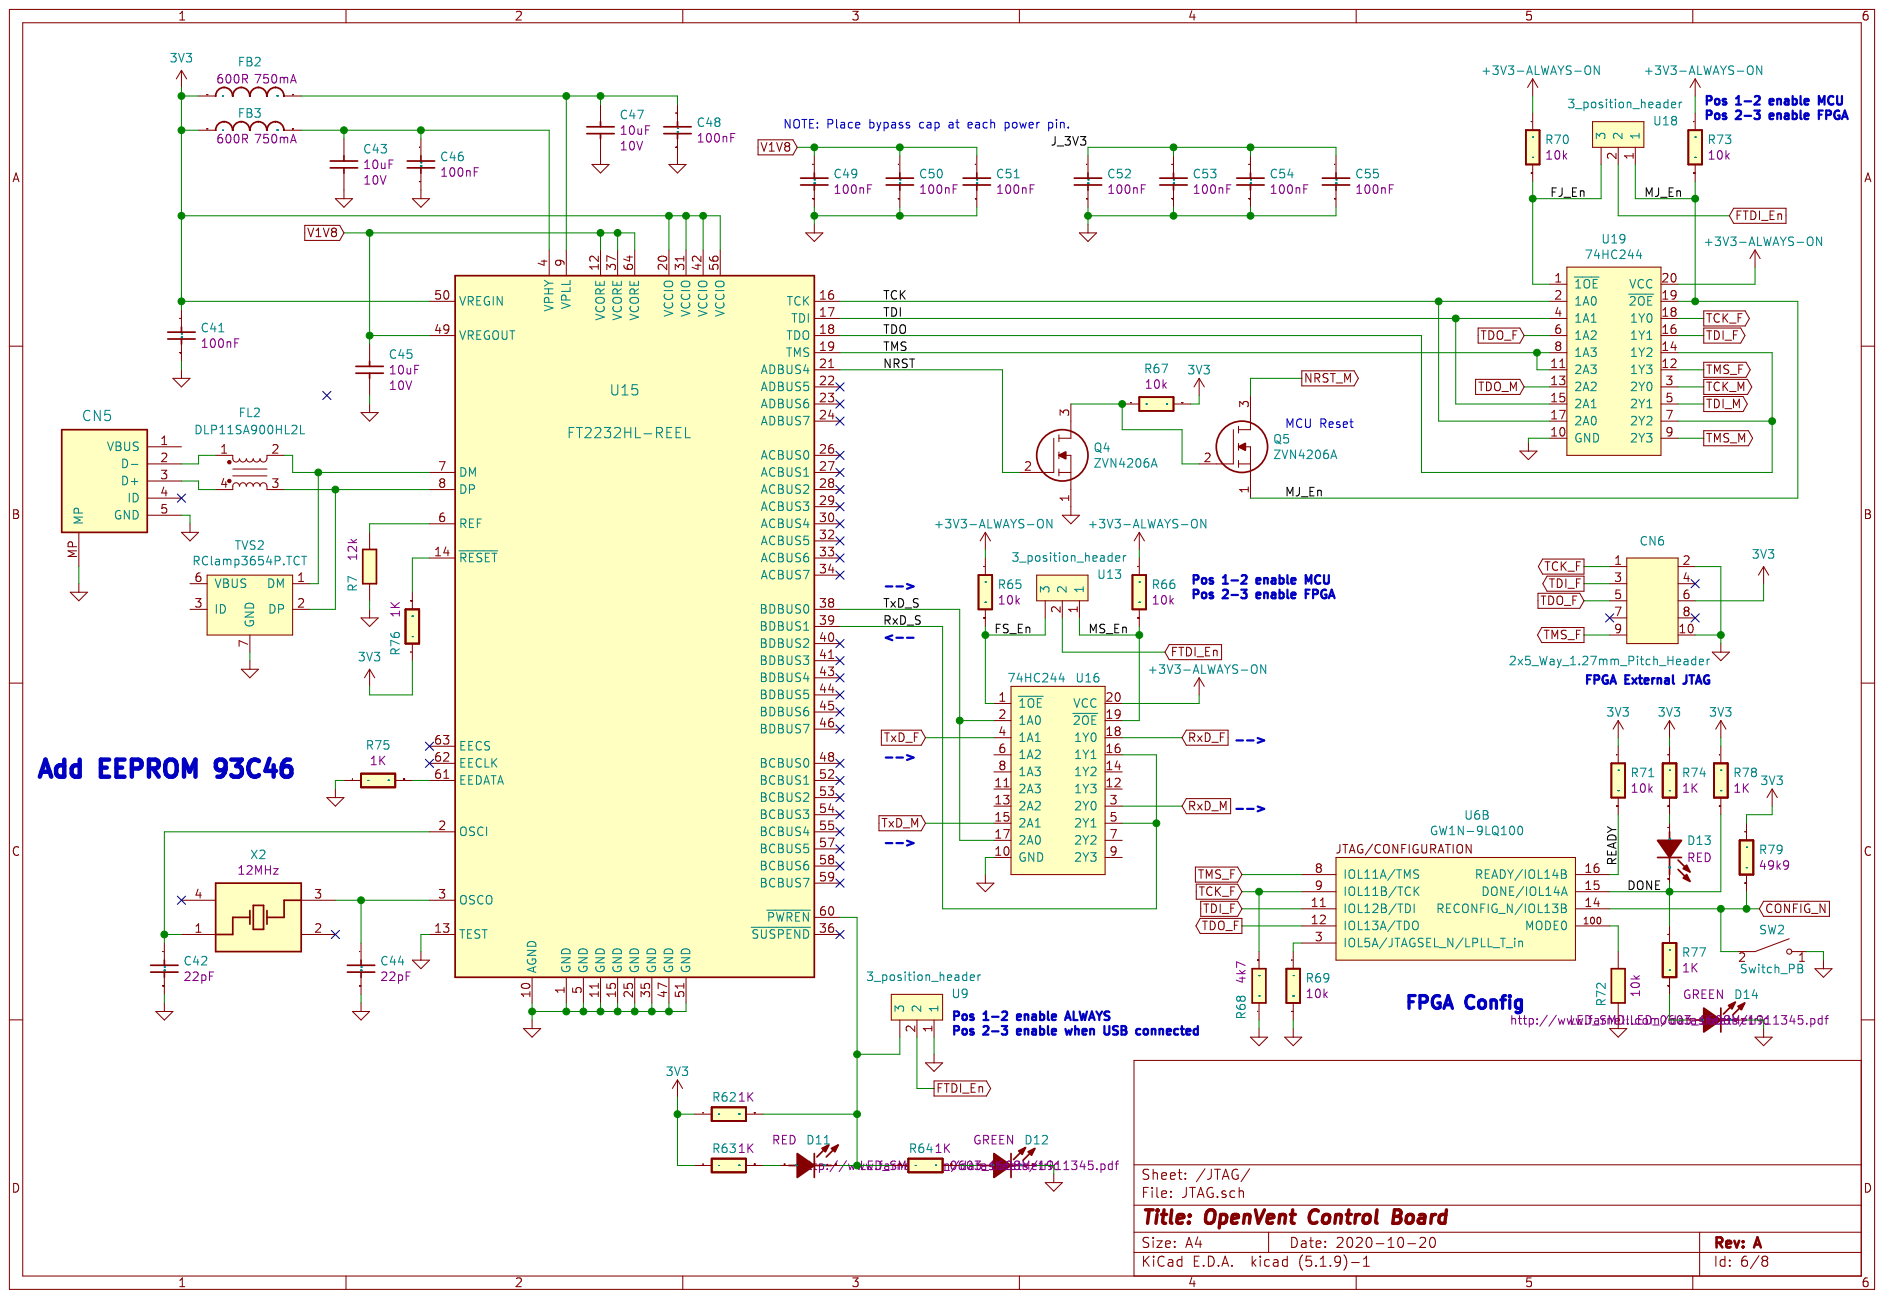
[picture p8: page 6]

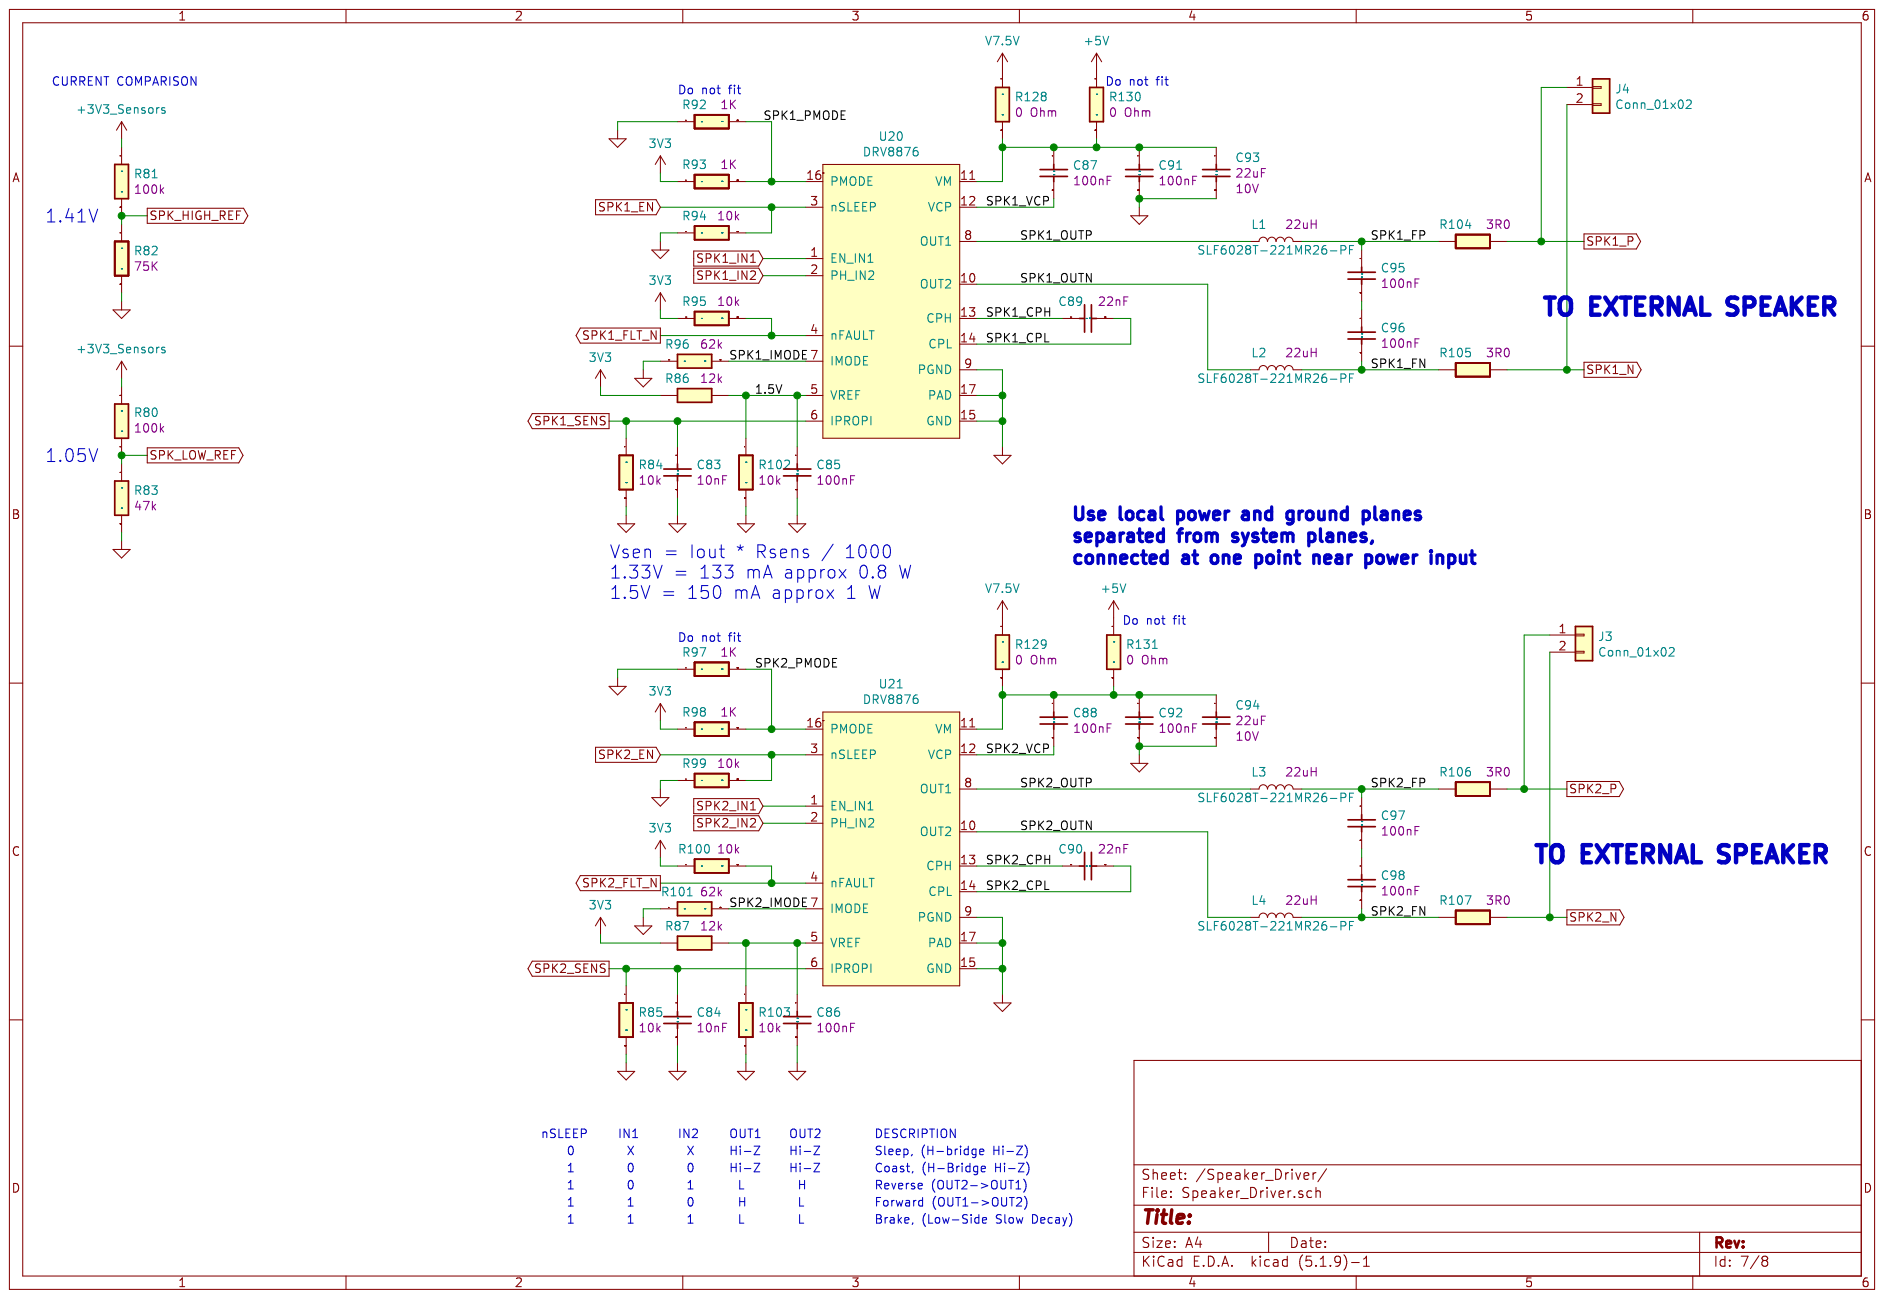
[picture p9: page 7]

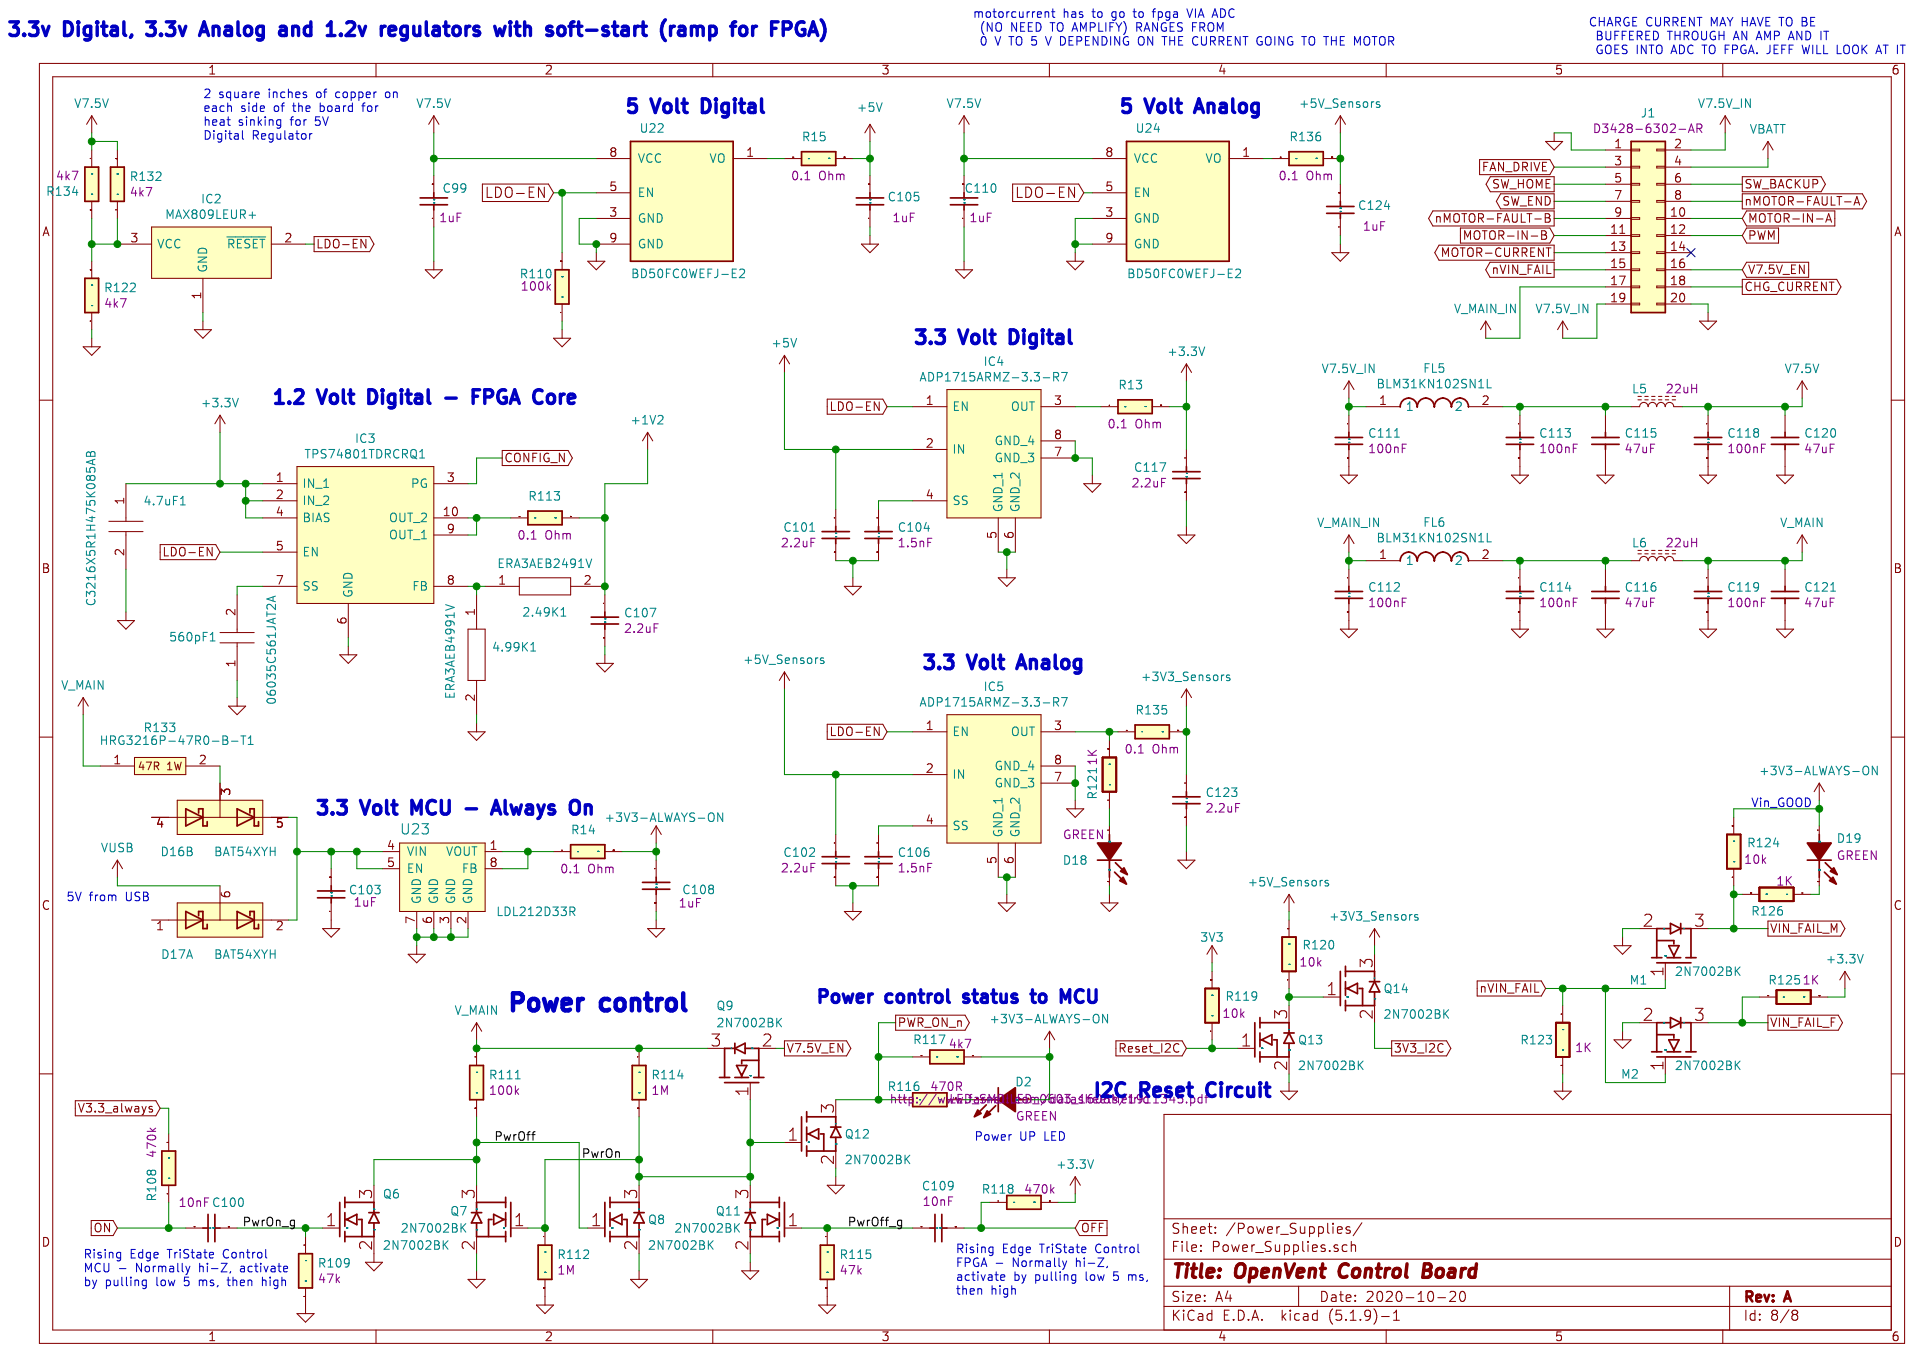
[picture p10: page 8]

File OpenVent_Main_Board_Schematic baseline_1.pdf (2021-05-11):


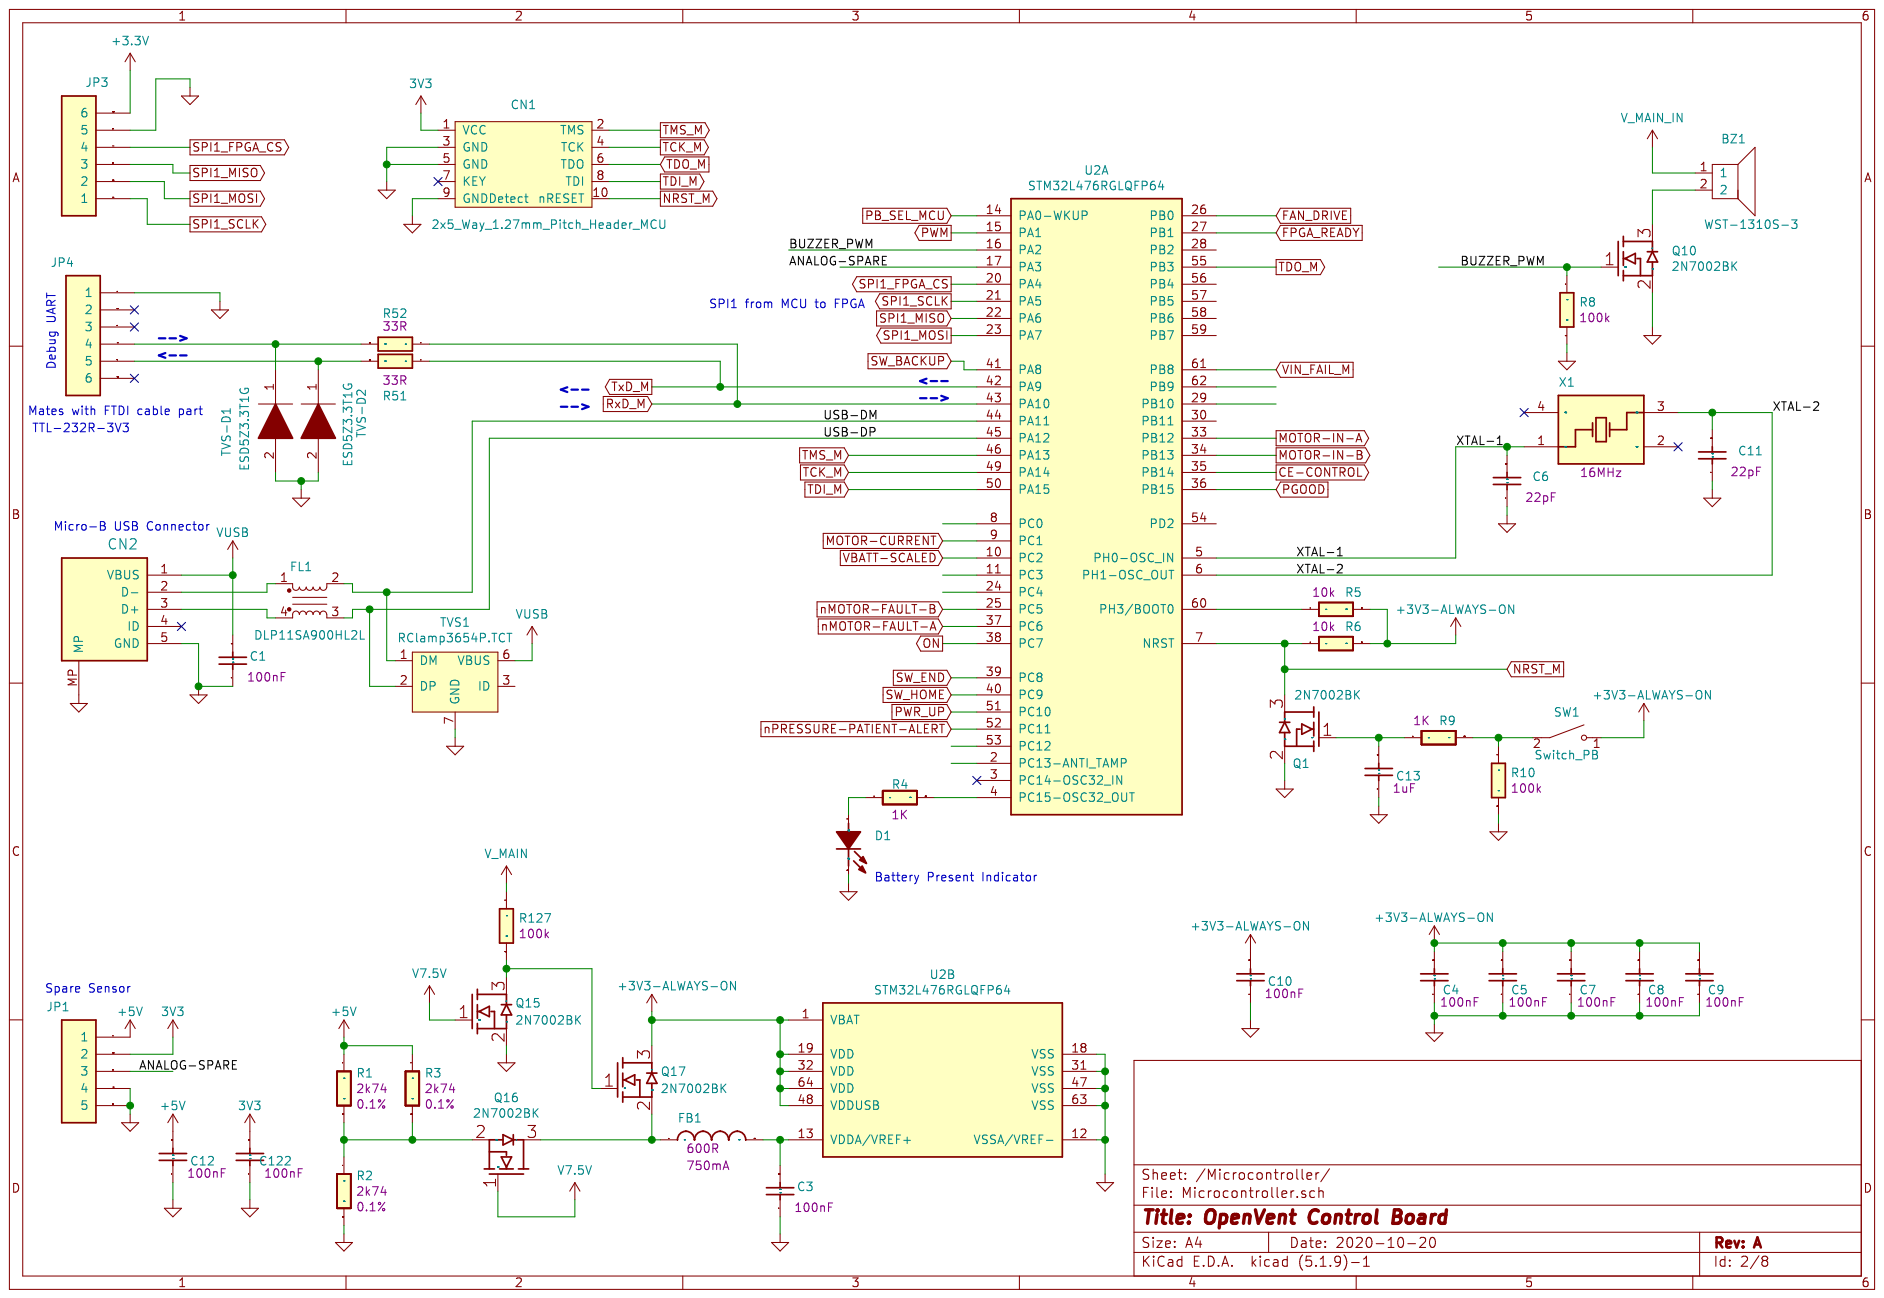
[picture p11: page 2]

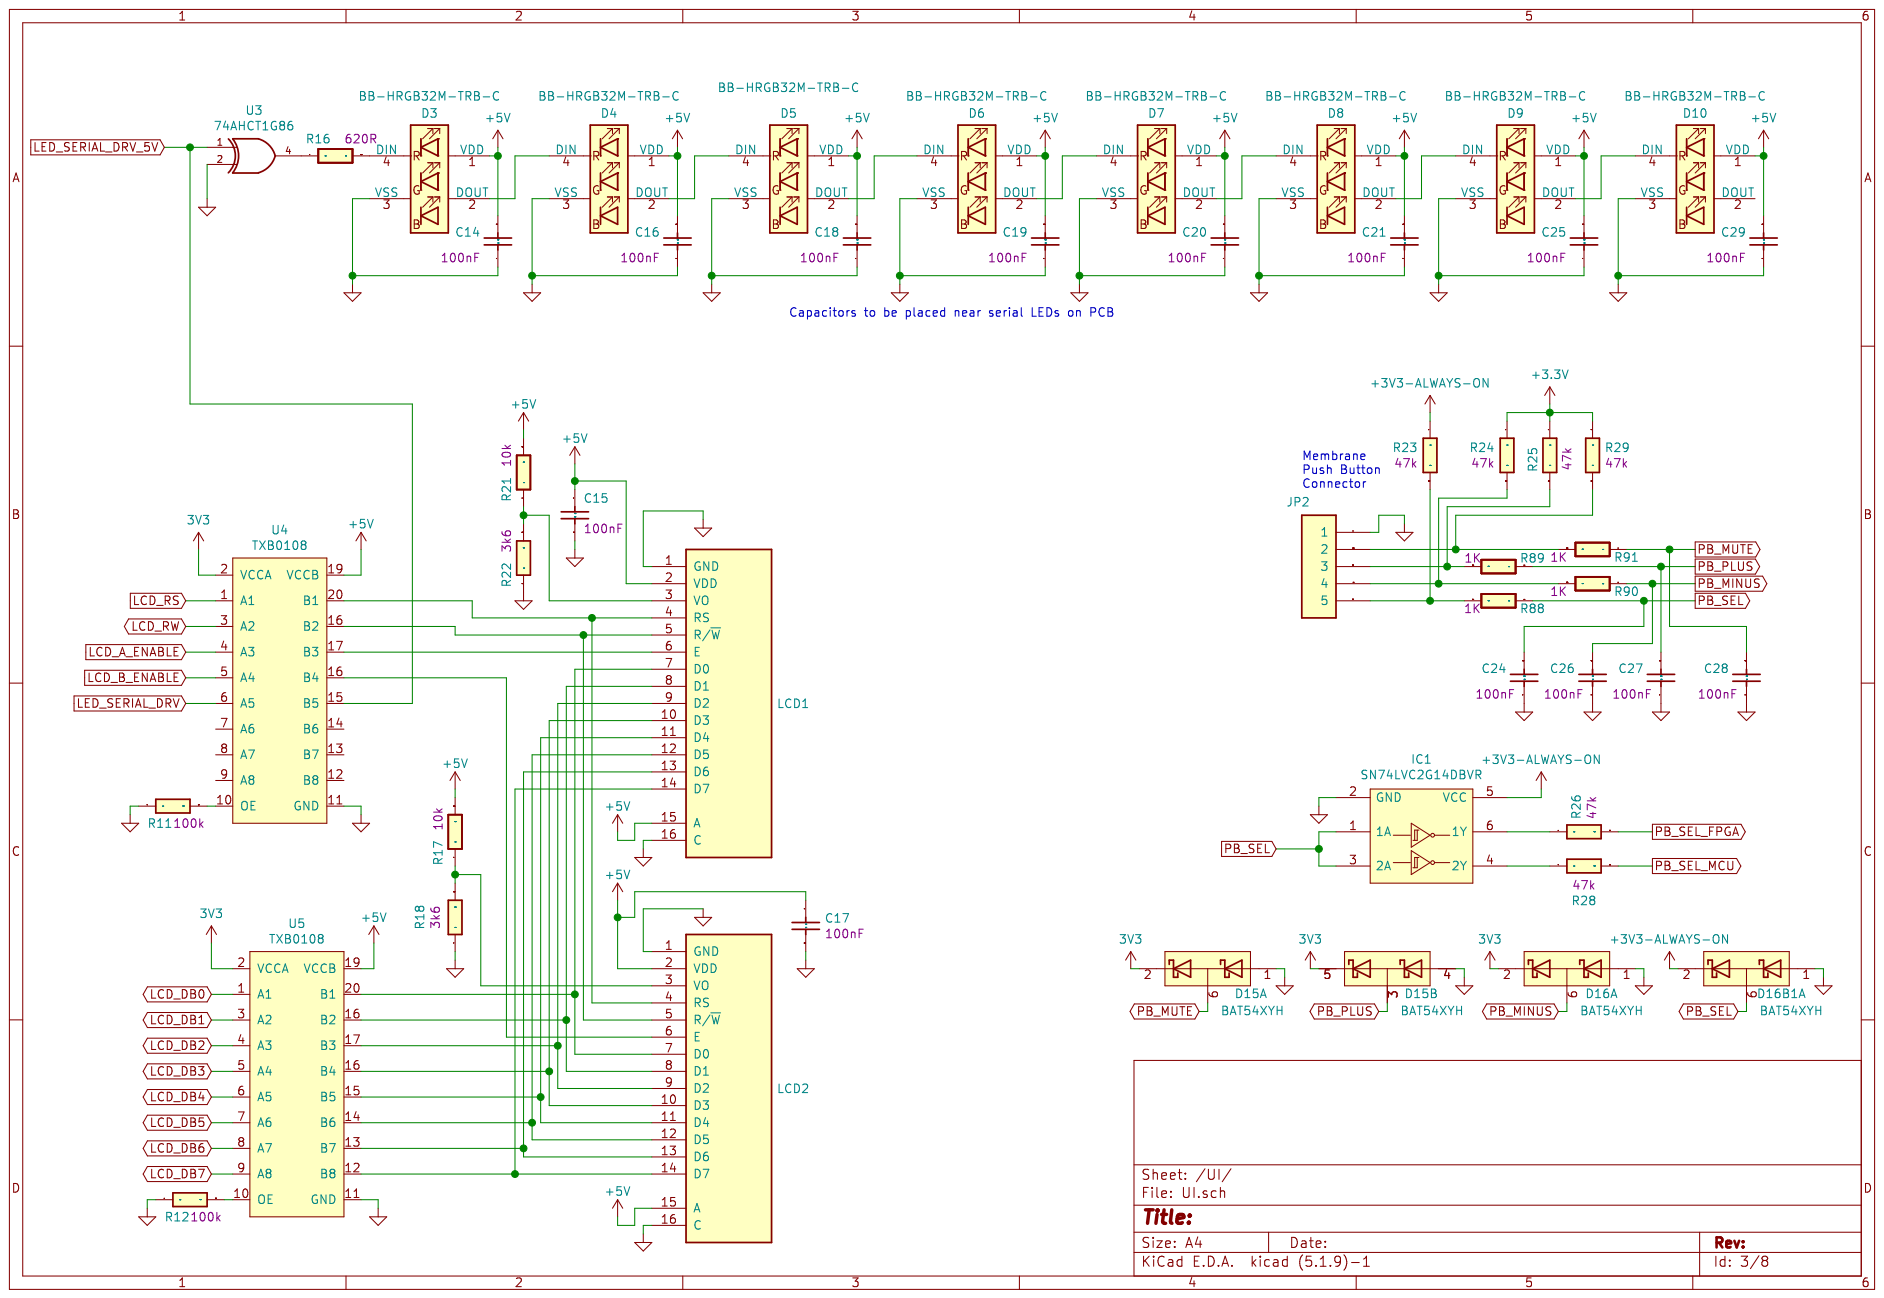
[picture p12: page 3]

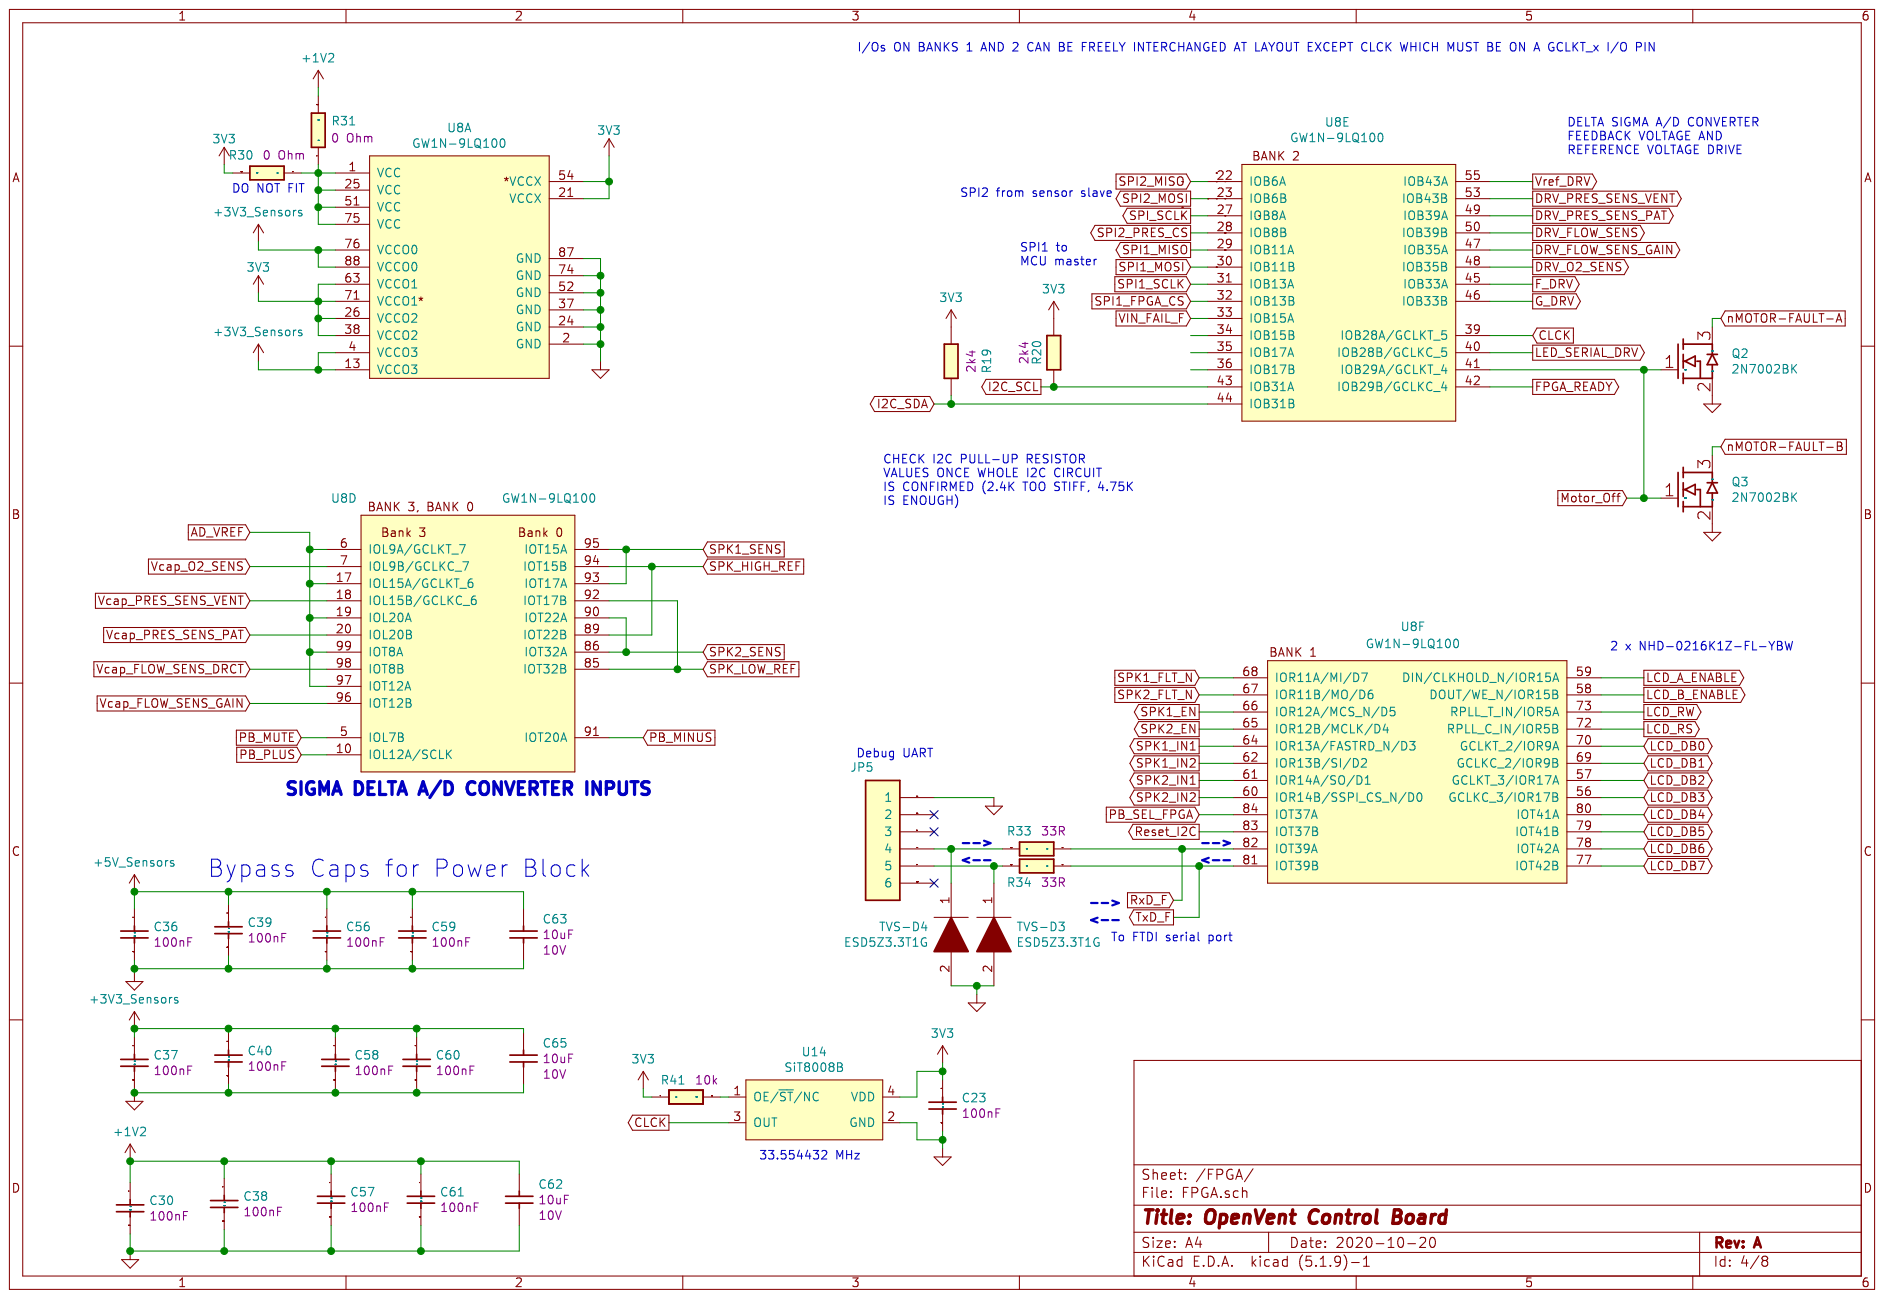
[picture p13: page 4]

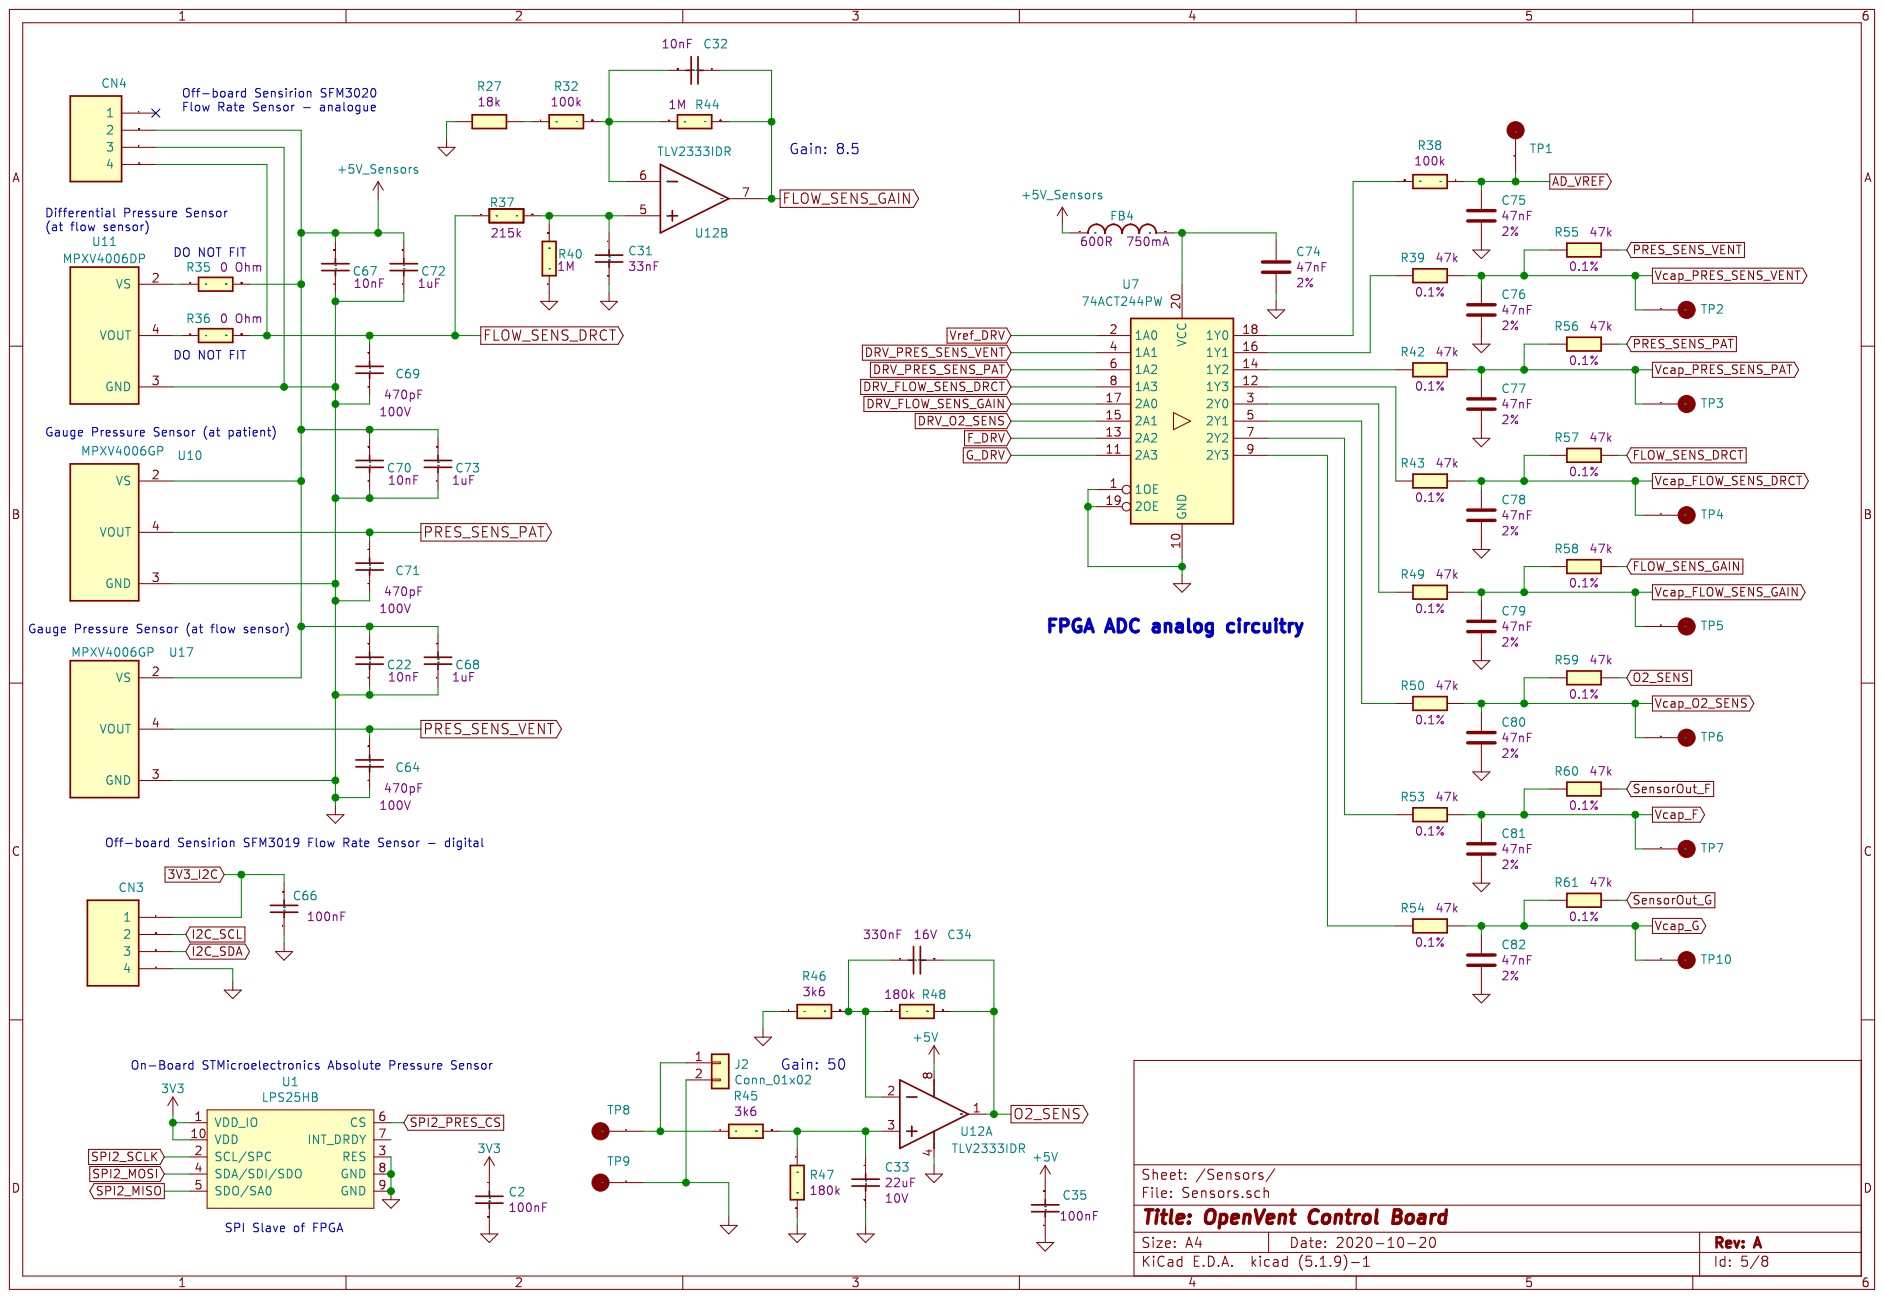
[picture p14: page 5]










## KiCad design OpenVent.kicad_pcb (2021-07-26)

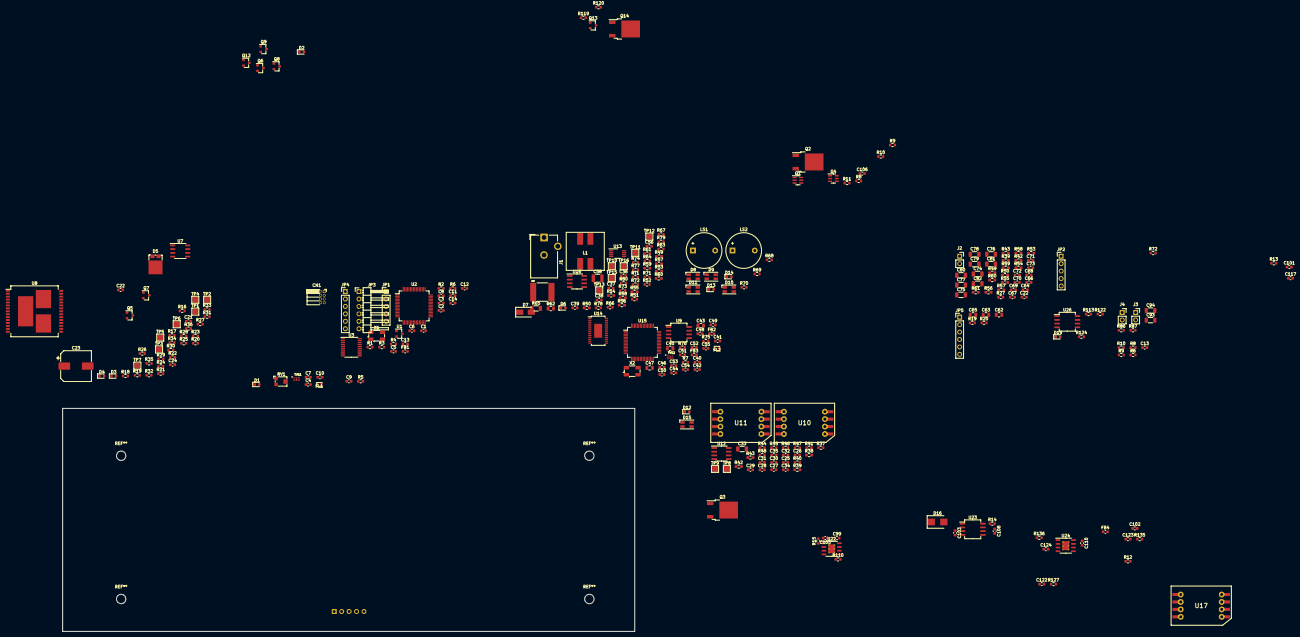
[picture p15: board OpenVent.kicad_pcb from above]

Board: 4 copper layers, 195.5 x 76.2 mm, 290 parts (0 on the bottom side), 143 nets, no tracks yet.

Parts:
C1, C2, C3, C4, C5, C7, C8, C9, C10, C12, C14, C35, C36, C38, C40, C41, C46, C48, C49, C50, C51, C52, C53, C54, C55, C66, C122: 100nF_0603_Ceramic_Capacitor,_10%,_X7R,_25V; C_0603_1608Metric
C6, C11, C42, C44: 22pF_0603_Ceramic_Capacitor,_5%,_NP0,_50V; C_0603_1608Metric
C13, C13#2, C29, C30, C39, C68, C72, C73, C99, C103, C105, C106, C108, C110, C124: 1uF_0603_Ceramic_Capacitor,_10%,_50V,_X5R; C_0603_1608Metric
C21, C26, C28, C64, C69, C71: 470pF_0603_Ceramic_Capacitor,_5%,_100V,_C0G; C_0603_1608Metric
C22, C22#2, C24, C25, C27, C32, C37, C56, C67, C70: 10nF_0603_Ceramic_Capacitor,_10%,_50V,_X7R-; C_0603_1608Metric
C23: 1000uF_25V_Aluminium_SMD_Capacitor,_20%; CP_Elec_10x10
C31: 33nF_0603_Ceramic_Capacitor,_10%,_50V; C_0603_1608Metric
C33: 22uF_1206_Ceramic_Capacitor,_10%,_10V,_X7R; C_1206_3216Metric
C34: 033uF_0603_Ceramic_Capacitor,_10%,_16V; C_0603_1608Metric
C43, C45, C47, C62, C63, C65: 10uF_0805_Ceramic_Capacitor_10%_X7R_10V; C_0805_2012Metric
C57: 2.2uF_2824_film_capacitor_10%_40V; CAPPC7360X380N
C58: C_1210_10uF_25V_10%_X7R; C_1210_3225Metric
C74, C75, C76, C77, C78, C79, C80, C81, C82: C_1206_47nF_16V_2%_PPS_film; C_1206_3216Metric
C93, C94: 22uF_1206_Ceramic_Capacitor,_10%,_10V,_X7R; R_1206_3216Metric
C101, C102, C117, C123: 2.2uF_0603_Ceramic_Capacitor,_10%,_50V,_X5R; C_0603_1608Metric
CN1: 2x5_Way_1.27mm_Pitch_Header_MCU; PinSocket_2x04_P1.27mm_Horizontal
D1, D2, D3, D6, D12, D14, D19: LED_GREEN_0603_SMD; LED_0603_1608Metric
D4, D13: LED_Red_0603_SMD; LED_0603_1608Metric
D5: FSV20100V; TO-277A
D7: DIODE_GEN_PURP_1KV_1A_SMA; D_SMA
D8, D9, D10, D11, D15: BB-HRGB32M-TRB; LED_RGB_BL-RRGB32M_TRB_PLCC4_3.2x2.8mm
D16: MBRS260T3G; D_SMB
FB1, FB2, FB3: Chip_Ferrite,_600R,_0603,_750mA; L_0603_1608Metric
FB4: BLM18AG601SN1D Chip_Ferrite,_600R,_0603,_750mA; C_0603_1608Metric
FL1, FL2: DLP11SA900HL2L; Murata_DLP11S
J1: OpenVent_Barrel_Connector; BarrelJack_CUI_PJ-102AH_Horizontal
J2, J3, J4: Conn_01x02; PinSocket_1x02_P2.54mm_Vertical
JP1, JP2, JP2#2: Pin_Header,_1x5-Way,_2.54mm_Pitch; PinHeader_1x05_P2.54mm_Vertical
JP3: Pin_Header,_1x6-Way,_2.54mm_Pitch, Mpn 640456-6; PinHeader_1x06_P2.54mm_Horizontal
JP4, JP5: Pin_Header,_1x6-Way,_2.54mm_Pitch; PinHeader_1x06_P2.54mm_Vertical
L1: MSD1260-333; MSD1260
LS1, LS2: AUDIO_MAGNETIC_INDICATOR; Buzzer_12x9.5RM7.6
Q1, Q4: DMMT5401-7-F; SC-74-6_1.5x2.9mm_P0.95mm
Q2, Q3, Q14: AOD4185; TO-252-2
Q5, Q6, Q7, Q9, Q12, Q13: 2N7002BK; SOT-23
Q8: SSM3K341R; SOT-23
R1, R2, R3: R_0603_2k74_0.1W_0.1%; R_0603_1608Metric
R4, R9, R9#2, R11, R12, R21, R22, R26, R28, R31, R71, R73, R74, R75, R76: 1K_0603_Chip_Resistor,_1%,_0.1W; R_0603_1608Metric
R5, R6, R6#2, R16, R18, R52, R119, R120, R124: 10k_0603_Chip_Resistor,_1%,_0.1W; R_0603_1608Metric
R7, R72, R72#2, R86, R87: 12k_0603_Chip_Resistor,_1%,_0.1W; R_0603_1608Metric
R8, R8#2, R10, R10#2, R29, R68, R69, R110, R127: 100K_0603_Chip_Resistor,_1%,_0.1W; R_0603_1608Metric
R13, R14, R15, R36, R113, R122, R135, R136: 0R1_0603_Chip_Resistor,_1%,_0.1W; R_0603_1608Metric
R17, R23, R37, R41, R67: 215k_0603_Chip_Resistor,_1%,_0.1W; R_0603_1608Metric
R19, R19#2, R20, R20#2: 2k4_0603_Chip_Resistor,_1%,_0.1W; R_0603_1608Metric
R24, R25: 4k7_0603_Chip_Resistor,_1%,_0.1W; R_0603_1608Metric
R27, R27#2: 18k_0603_Chip_Resistor,_1%,_0.1W; R_0603_1608Metric
R30, R32, R35: 30k_0603_Chip_Resistor,_1%,_0.1W; R_0603_1608Metric
R33, R34: 20k_0603_Chip_Resistor,_1%,_0.1W; R_0603_1608Metric
R38, R39, R39#2, R42, R42#2, R43, R43#2, R49, R49#2, R50, R50#2, R53, R53#2, R54, R54#2, R55, R55#2, R56, R56#2, R57, R57#2, R58, R58#2, R59, R59#2, R60, R60#2, R61, R61#2: R_0603_47K_0.1%_0.1W_Film; R_0603_1608Metric_Pad0.98x0.95mm_HandSolder
R40, R44, R66: 1M_0603_Chip_Resistor,_1%,_0.1W; R_0603_1608Metric
R45, R46: 3k6_0603_Chip_Resistor,_1%,_0.1W; R_0603_1608Metric
R47, R48: 180k_0603_Chip_Resistor,_1%,_0.1W; R_0603_1608Metric
R51: 634R_0603_Chip_Resistor,_1%,_0.1W; R_0603_1608Metric
R62: R_0805_050m_cursense; R_0805_2012Metric
R63: R_0603_015m_cursense; R_0603_1608Metric
R64: R_0603_49k9_0.1W_1%; R_0603_1608Metric
R65: R_1206_250m_cursense; R_1206_3216Metric
R70: 10R_0603_Chip_Resistor,_1%,_0.1W; R_0603_1608Metric
R77: R_0603_113k_0.1W_1%; R_0603_1608Metric
R78: R_0603_30k1_0.1W_1%; R_0603_1608Metric
R79: R_0603_95k3_0.1W_1%; R_0603_1608Metric
R80: R_0603_10k2_0.1W_1%; R_0603_1608Metric
RT1: R_Thermistor_0603_10K_NTC; R_0603_1608Metric
RV1: RES_trimpot_10K_SMD; Potentiometer_Bourns_TC33X_Vertical
TP1, TP2, TP3, TP4, TP5, TP6, TP7, TP8, TP9, TP10, TP11, TP12, TP13, TP15, TP16: Test_Point_PTH; TestPoint_Pad_2.0x2.0mm
TVS1, TVS2: RClamp3654P.TCT; SON50P160X160X65-7N
U1: TMP236A4DBZT; SOT-23
U2: STM32L476RGLQFP64; LQFP-64_10x10mm_P0.5mm
U3: TI_TXB0108PWR; TSSOP-20_4.4x6.5mm_P0.65mm
U7: LMC6772AIMX; SO-8_3.9x4.9mm_P1.27mm
U8: VNH5019ATR-E; ST_MultiPowerSO-30
U9, U23, U26: LDL212D33R; SO-8_5.3x6.2mm_P1.27mm
U10, U17: MPXV4006GP; NXP-CASE-1369_482C
U11: MPXV4006DP; NXP-CASE-1351-482C
U12, U16: TLV2333IDR; SOIC-8_3.9x4.9mm_P1.27mm
U13: TLV7042DGKR; VSSOP-8_3.0x3.0mm_P0.65mm
U14: LT3796; TSSOP-28-LTvar_EB_4.4x9.7mm_P0.65mm
U15: FT2232HL-REEL; LQFP-64_10x10mm_P0.5mm
U22, U24: BD50FC0WEFJ-E2; HSOP-8-1EP_3.9x4.9mm_P1.27mm_EP2.41x3.1mm_ThermalVias
X1: ABM3B-16.000MHZ; Crystal_SMD_Abracon_ABM3B-4Pin_5.0x3.2mm
X2: ABM3B-12.000MHZ; Crystal_SMD_Abracon_ABM3B-4Pin_5.0x3.2mm

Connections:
+3.3V: C65.1, C123.1, R122.2, R135.2
+3V3: C2.2, C41.1, C106.2, C117.1, C122.2, CN1.1, FB2.1, FB3.1, JP1.2, JP3.6, R13.2, R19.2, R19#2.2, R20.2, R20#2.2, R24.2, R25.2, R52.1, R71.1, R73.1, R76.1, R86.1, R87.1, R119.2, TP10.1, U1.1, U3.2, U3.10, U7.6, U13.8, U15.20, U15.31, U15.42, U15.50, U15.56
+5V: C12.2, C14.2, C22.2, C22#2.2, C25.2, C27.2, C29.2, C30.2, C35.2, C62.1, C63.1, C67.2, C68.2, C70.2, C72.2, C73.2, C99.2, C101.1, C102.1, C105.2, C110.2, C124.2, D8.1, D9.1, D10.1, D11.1, D15.1, FB4.1, JP1.1, LS1.1, LS2.1, R1.1, R3.1, R15.2, R29.2, R69.2, R113.2, R120.2, R136.2, RV1.1, TP11.1, U3.19, U7.8, U10.2, U12.8, U17.2, U22.8, U24.8, U26.4
/JTAG/J_3V3: C52.1, C53.1, C54.1, C55.1, U9.1, U9.8
/Microcontroller/ANALOG-SPARE: JP1.3, U2.17
/Microcontroller/BUZZER_PWM: R8.1, R8#2.1, U2.16
/Microcontroller/USB-DM: FL1.2, TVS1.1, U2.44
/Microcontroller/USB-DP: FL1.3, TVS1.2, U2.45
/Microcontroller/XTAL-1: C6.2, U2.5, X1.1
/Microcontroller/XTAL-2: C11.2, U2.6, X1.3
/Power_Supplies/3v3_S: R122.1, U26.1, U26.8
AD_VREF: C75.1, R38.2
FLOW_SENS_DRCT: C69.2, R37.1, R57.1, R57#2.1
FLOW_SENS_GAIN: C32.1, R44.2, R58.1, R58#2.1, U12.7
GND: C1.1, C2.1, C3.1, C4.1, C5.1, C6.1, C7.1, C8.1, C9.1, C10.1, C11.1, C12.1, C13.1, C13#2.1, C14.1, C22.1, C22#2.1, C25.1, C26.1, C27.1, C28.1, C29.1, C30.1, C31.2, C33.2, C35.1, C36.2, C37.2, C38.2, C39.2, C40.2, C41.2, C42.2, C43.2, C44.2, C45.2, C46.2, C47.2, C48.2, C49.2, C50.2, C51.2, C52.2, C53.2, C54.2, C55.2, C56.2, C58.2, C62.2, C63.2, C64.1, C65.2, C66.1, C67.1, C68.1, C69.1, C70.1, C71.1, C72.1, C73.1, C74.2, C75.2, C76.2, C77.2, C78.2, C79.2, C80.2, C81.2, C82.2, C93.2, C94.2, C99.1, C101.2, C102.2, C103.1, C105.1, C106.1, C108.2, C110.1, C117.2, C122.1, C123.2, C124.1, CN1.3, CN1.5, D1.2, D5.1, D5.2, D8.3, D9.3, D10.3, D11.3, D12.2, D14.2, D15.3, J1.2, J2.2, JP1.4, JP1.5, JP2.1, JP2#2.1, JP3.5, JP4.1, JP5.1, L1.4, Q5.2, Q9.2, Q12.2, R2.2, R7.1, R8.2, R8#2.2, R10.2, R10#2.2, R11.1, R12.1, R18.2, R27.1, R27#2.1, R33.2, R34.2, R40.1, R41.1, R46.1, R47.2, R63.1, R67.2, R68.2, R70.2, R72.1, R72#2.1, R74.1, R75.1, R80.2, R110.1, RV1.3, TP2.1, TP9.1, TP13.1, TP16.1, TVS1.7, TVS2.7, U1.3, U2.12, U2.18, U2.31, U2.47, U2.63, U3.11, U7.4, U7.5, U9.2, U9.3, U9.6, U9.7, U10.3, U11.3, U12.4, U13.4, U14.4, U14.13, U14.17, U14.21, U14.22, U14.29, U15.1, U15.5, U15.10, U15.11, U15.13, U15.15, U15.25, U15.35, U15.47, U15.51, U16.4, U17.3, U22.3, U22.9, U23.2, U23.3, U23.6, U23.7, U24.3, U24.9, U26.2, U26.3, U26.6, U26.7
I2C_SCL: R20.1, R20#2.1
I2C_SDA: R19.1, R19#2.1
LDO-EN: R110.2, U22.5, U24.5
MOTOR-CURRENT: C21.2, R23.1, TP3.1, U2.9, U7.1
MOTOR-IN-B: R21.1, U2.34
NRST_M: R6.1, R6#2.1, U2.7
unnamed: C3.2, FB1.2, U2.13
unnamed: C13.2, C13#2.2, R9.1, R9#2.1
unnamed: C21.1, R18.1, R23.2, U7.2
unnamed: C24.1, Q7.1, R34.1, R35.1, TP7.1
unnamed: C31.1, R37.2, R40.2, U12.5
unnamed: C32.2, R41.2, R44.1, U12.6
unnamed: C33.1, R45.2, R47.1, U12.3
unnamed: C34.1, R46.2, R48.1, U12.2
unnamed: C36.1, R52.2, U13.3
unnamed: C37.1, U14.28
unnamed: C38.1, U14.11
unnamed: C40.1, U9.4, U9.5
unnamed: C42.1, U15.2, X2.1
unnamed: C43.1, C46.1, FB3.2, U15.4
unnamed: C44.1, U15.3, X2.3
unnamed: C47.1, C48.1, FB2.2, U15.9
unnamed: C57.1, L1.1, Q8.3
unnamed: C57.2, D16.2, L1.2
unnamed: C58.1, D16.1, R65.1, U14.1
unnamed: C74.1, FB4.2
unnamed: C103.2, U23.4, U23.5
unnamed: U8.15, U8.16, U8.21
unnamed: U8.1, U8.25, U8.30
unnamed: D1.1, R4.1
unnamed: Q1.5, Q2.3, Q3.3, Q4.5
unnamed: D5.3, R36.1
unnamed: D7.1, R65.2, R78.1, RT1.1, U14.2
unnamed: D10.2, D11.4
unnamed: D9.2, D10.4
unnamed: D11.2, U15.60
unnamed: FL2.2, TVS2.1, U15.7
unnamed: FL2.3, TVS2.2, U15.8
unnamed: J2.1, R45.1, TP8.1
unnamed: JP2.2, JP2#2.2
unnamed: JP2.3, JP2#2.3
unnamed: JP2.4, JP2#2.4
unnamed: JP2.5, JP2#2.5
unnamed: L1.3, R62.2, U14.26
unnamed: LS1.2, LS2.2, Q13.3
unnamed: Q1.1, Q1.2, Q1.3
unnamed: Q1.4, Q3.1
unnamed: Q2.1, Q4.4
unnamed: Q4.1, Q4.2, Q4.3
unnamed: Q5.3, Q6.1, R29.1
unnamed: Q6.2, Q7.2, R33.1, TP6.1
unnamed: Q7.3, R32.1, TP5.1
unnamed: Q8.1, U14.19
unnamed: Q8.2, R63.2, U14.18
unnamed: Q9.1, R68.1
unnamed: Q12.1, R64.2, U14.16
unnamed: Q12.3, R77.2
unnamed: Q9.3, Q13.1, R69.1
unnamed: Q6.3, Q14.1, R30.1, TP4.1
unnamed: R1.2, R2.1, R3.2
unnamed: R4.2, U2.4
unnamed: R5.1, U2.60
unnamed: R7.2, U15.6
unnamed: R9.2, R9#2.2, R10.1, R10#2.1
unnamed: R14.1, U23.1, U23.8
unnamed: R15.1, U22.1
unnamed: R16.1, R17.1, U7.3
unnamed: R16.2, TP1.1, U8.18, U8.19, U8.20, U8.26, U8.27, U8.28
unnamed: R21.2, U8.10
unnamed: R22.2, U8.7
unnamed: R27.2, R27#2.2
unnamed: R39.2, R39#2.2
unnamed: R42.2, R42#2.2
unnamed: R43.2, R43#2.2
unnamed: R49.2, R49#2.2, U13.2
unnamed: R50.2, R50#2.2
unnamed: R53.2, R53#2.2, U14.6
unnamed: R54.2, R54#2.2
unnamed: R64.1, U14.20
unnamed: R66.2, R67.1, U16.3
unnamed: R71.2, U13.6
unnamed: R72.2, R72#2.2, U13.5
unnamed: R73.2, U16.6
unnamed: R74.2, U16.5
unnamed: R75.2, U15.61
unnamed: R76.2, U15.14
unnamed: R77.1, R79.2, R80.1, U14.7
unnamed: R78.2, R79.1, RT1.2
unnamed: R136.1, U24.1
unnamed: U2.28, U3.4
unnamed: U2.56, U3.6
unnamed: U2.57, U3.7
unnamed: U2.58, U3.8
unnamed: U2.59, U3.9
unnamed: U14.9, U14.10, U14.14
O2_SENS: C34.2, R48.2, R59.1, R59#2.1, U12.1
PB_SEL_MCU: R28.2, U2.14
PRES_SENS_PAT: C71.2, R56.1, R56#2.1, U10.4
PRES_SENS_VENT: C64.2, R55.1, R55#2.1, U17.4
PWM: R22.1, U2.15
SOUNDER-CURRENT: Q13.2, R70.1
SPI1_FPGA_CS: JP3.4, U2.20
SPI1_MISO: JP3.3, U2.22
SPI1_MOSI: JP3.2, U2.23
SPI1_SCLK: JP3.1, U2.21
SensorOut_F: R60.1, R60#2.1
SensorOut_G: R61.1, R61#2.1
TCK_M: CN1.4, U2.49
TDI_M: CN1.8, U2.50
TDO_M: CN1.6, U2.55
TMS_M: CN1.2, U2.46
V1V8: C45.1, C49.1, C50.1, C51.1, U15.12, U15.37, U15.49, U15.64
VBATT-SCALED: U2.10, U16.1, U16.2
VBUS: C39.1, D7.2, Q4.6, R66.1, TP12.1, TP15.1
VDC: C4.2, C5.2, C7.2, C8.2, C9.2, C10.2, C108.1, D2.1, D19.1, R5.2, R6.2, R6#2.2, R14.2, R124.2, U2.1, U2.19, U2.32, U2.48, U2.64, U16.8
VIN: J1.1, R51.1, R62.1, U14.23, U14.25
VIN_FAIL_M: R124.1, U2.61
VMEM: C1.2, Q1.6, TVS1.6
VMOTOR: C24.2, R35.2, R36.2, U8.3, U8.12, U8.13, U8.23
Vcap_F: C81.1, R53.1, R53#2.1, R60.2, R60#2.2
Vcap_FLOW_SENS_DRCT: C78.1, R43.1, R43#2.1, R57.2, R57#2.2
Vcap_FLOW_SENS_GAIN: C79.1, R49.1, R49#2.1, R58.2, R58#2.2
Vcap_G: C82.1, R54.1, R54#2.1, R61.2, R61#2.2
Vcap_O2_SENS: C80.1, R50.1, R50#2.1, R59.2, R59#2.2
Vcap_PRES_SENS_PAT: C77.1, R42.1, R42#2.1, R56.2, R56#2.2
Vcap_PRES_SENS_VENT: C76.1, R39.1, R39#2.1, R55.2, R55#2.2
nMOTOR-FAULT-A: R25.1, U2.37, U8.5
nMOTOR-FAULT-B: R24.1, U2.25, U8.9

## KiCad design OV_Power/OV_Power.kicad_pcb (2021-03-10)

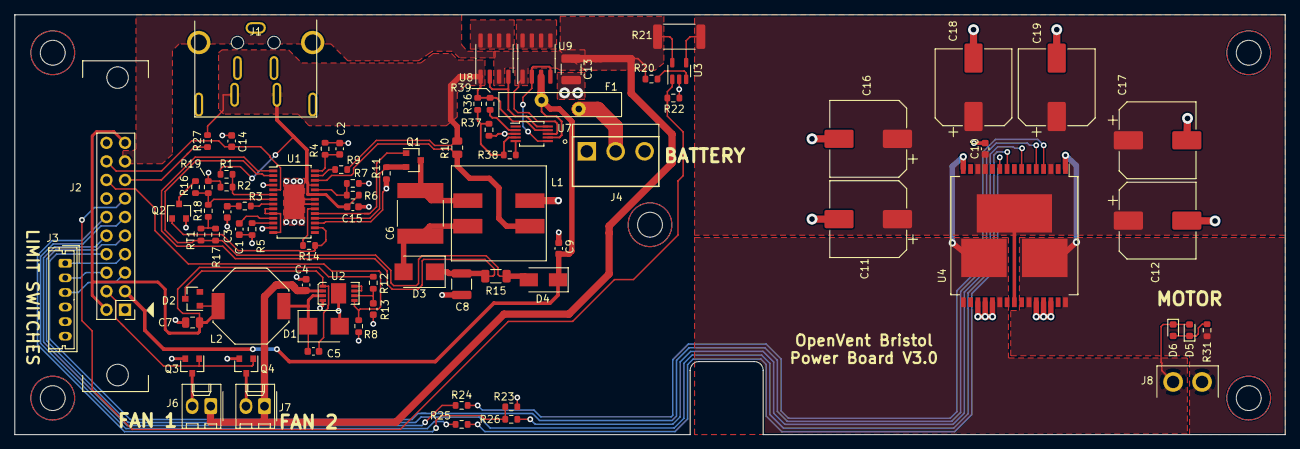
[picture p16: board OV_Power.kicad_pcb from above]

Board: 2 copper layers, 174.0 x 57.5 mm, 79 parts (0 on the bottom side), 61 nets.

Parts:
C1, C4, C10, C14, C15: 100nF_0603_Ceramic_Capacitor,_10%,_X7R,_25V; C_0603_1608Metric
C2, C3: 10nF_0603_Ceramic_Capacitor,_10%,_50V,_X7R-; C_0603_1608Metric
C5: C_0603_0.22uf_25V_10%; C_0603_1608Metric
C6: 2.2uF_2824_film_capacitor_10%_40V; CAPPC7360X380N
C7: 10uF_0805_Ceramic_Capacitor_10%_X7R_10V; C_0805_2012Metric
C8, C13: C_1210_10uF_25V_10%_X7R; C_1210_3225Metric
C9: 1uF_0603_Ceramic_Capacitor,_10%,_50V,_X5R; C_0603_1608Metric
C11, C12, C16, C17, C18, C19: 1000uF_25V_Aluminium_SMD_Capacitor,_20%; CP_Elec_10x10
D1, D3: MBRS260T3G; D_SMB
D2: MMBD914; SOT-23
D4: S1B; D_SMA
D5: LED_GREEN_0603_SMD; LED_0603_1608Metric
D6: LED_Red_0603_SMD; LED_0603_1608Metric
F1: Polyfuse_10A; LF_16R1000G
J1: Kycon_kpjx-4s_shielded; Kycon_KPJX-4S_SHIELD
J2: Conn_HDR_2x10_latching; 3M_D3428-6302-AR
J3: 532530670; Molex_Micro-Latch_53253-0670_1x06_P2.00mm_Vertical
J4: Conn_01x03_JST_B3P_Vert; JST_B3P-VH(LF)(SN)
J6, J7: CONN_HEADER_2.54X2_MOLEX_KK_Series; Molex_KK-254_AE-6410-02A_1x02_P2.54mm_Vertical
J8: CONN_HEADER_R_A_2POS_JST_10A; JST_B2PS-VHLSN
L1: MSD1260-333; MSD1260
L2: L_22uH_2.6A_42mOhm_SMT; L-Bourns-SRU1048-series
Q1: SSM3K341R; SOT-23
Q2: 2N7002BK; SOT-23
Q3, Q4: SZNUD3124LT1G; SOT-23
R1: R_0603_806K_0.1W_1%; R_0603_1608Metric
R2: 20k_0603_Chip_Resistor,_1%,_0.1W; R_0603_1608Metric
R3: R_0603_499R_0.1W_1%; R_0603_1608Metric
R4: R_0603_40k2K_0.1W_1%; R_0603_1608Metric
R5: R_0603_19k6_0.1W_1%; R_0603_1608Metric
R6: R_0603_499K_0.1W_1%; R_0603_1608Metric
R7: R_0603_97.6K_0.1W_1%; R_0603_1608Metric
R8: 100K_0603_Chip_Resistor,_1%,_0.1W; R_0603_1608Metric
R9: R_0603_2k_0.1W_1%; R_0603_1608Metric
R10: R_0805_050m_cursense; R_0805_2012Metric
R11: R_0603_015m_cursense; R_0603_1608Metric
R12: R_0603_53K_0.1W_1%; R_0603_1608Metric
R13: 10k_0603_Chip_Resistor,_1%,_0.1W; C_0603_1608Metric
R14: R_0603_49k9_0.1W_1%; R_0603_1608Metric
R15: R_1206_250m_cursense; R_1206_3216Metric
R16: R_0603_113k_0.1W_1%; R_0603_1608Metric
R17: R_0603_30k1_0.1W_1%; R_0603_1608Metric
R18: R_0603_95k3_0.1W_1%; R_0603_1608Metric
R19: R_0603_10k2_0.1W_1%; R_0603_1608Metric
R20: R_0603_100_0.1W_0.1%; R_0603_1608Metric
R21: R_2512_15m_cursense; R_2512_6332Metric
R22: R_0603_2k74_0.1W_0.1%; R_0603_1608Metric
R23, R24, R25, R26, R27, R31: 1K_0603_Chip_Resistor,_1%,_0.1W; R_0603_1608Metric
R36: R_0603_178K_0.1W_1%; R_0603_1608Metric
R37: R_0603_24k9_0.1W_1%; R_0603_1608Metric
R38: R_0603_221K_0.1W_1%; R_0603_1608Metric
R39: 10k_0603_Chip_Resistor,_1%,_0.1W; R_0603_1608Metric
RT1: R_Thermistor_0603_10K_NTC; R_0603_1608Metric
U1: LT3796; TSSOP-28-LTvar_EB_4.4x9.7mm_P0.65mm
U2: LT1936; LT_MS8E
U3: LT6106; TSOT-23-5
U4: VNH5019ATR-E; ST_MultiPowerSO-30
U7: LTC4416; MSOP-10_3x3mm_P0.5mm
U8, U9: AOSD21307; SOIC-8_3.9x4.9mm_P1.27mm

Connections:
/ISP_N: D4.2, R15.2, R17.1, RT1.1, U1.2
/ISP_P: C8.1, D3.1, R15.1, U1.1
/Power Supply/FAN_DRIVE: J2.4, Q3.1, Q4.1
/Power Supply/POWER_STATUS: J2.15, R27.1
CHG_CURRENT: C14.1, J2.18, U1.5
GND: C1.2, C2.2, C3.2, C4.2, C7.2, C8.2, C9.2, C10.2, C11.2, C12.2, C13.2, C14.2, C15.2, C16.2, C17.2, C18.2, C19.2, D1.2, J1.3, J1.4, J1.5, J1.6, J1.7, J1.8, J2.1, J2.20, J3.4, J3.5, J3.6, J4.1, J4.3, L1.4, Q2.2, Q3.2, Q4.2, R2.2, R4.2, R5.2, R7.2, R8.2, R11.1, R13.2, R19.2, R22.2, R23.1, R37.2, U1.4, U1.13, U1.17, U1.21, U1.22, U1.29, U2.4, U2.9, U3.2, U4.18, U4.19, U4.20, U4.26, U4.27, U4.28, U7.3
MOTOR-IN-A: J2.10, R24.1
MOTOR-IN-B: J2.11, R25.1
MOTOR_CURRENT: J2.13, R22.1, U3.1
unnamed: C1.1, U1.11
unnamed: C2.1, R4.1, U1.28
unnamed: C3.1, R3.2
unnamed: C5.1, D2.3, U2.1
unnamed: C5.2, D1.1, L2.1, U2.3
unnamed: C6.1, L1.1, Q1.3
unnamed: C6.2, D3.2, L1.2
unnamed: C10.1, C11.1, C12.1, C16.1, C17.1, C18.1, C19.1, R21.2, U3.4, U4.3, U4.12, U4.13, U4.23, U4.31
unnamed: D5.1, D6.2, R31.2
unnamed: D5.2, D6.1, J8.1, U4.15, U4.16, U4.21, U4.32
unnamed: F1.1, J4.2
unnamed: J2.5, J3.3
unnamed: J2.6, J3.2
unnamed: J2.7, J3.1
unnamed: J6.2, Q3.3
unnamed: J7.2, Q4.3
unnamed: J8.2, R31.1, U4.1, U4.25, U4.30, U4.33
unnamed: L1.3, R10.2, U1.26
unnamed: Q1.1, U1.19
unnamed: Q1.2, R11.2, U1.18
unnamed: Q2.1, R14.2, U1.16
unnamed: Q2.3, R16.2
unnamed: R1.2, R2.1, U1.6
unnamed: R3.1, U1.8
unnamed: R5.1, U1.12
unnamed: R6.2, R7.1, U1.24
unnamed: R9.2, U1.27
unnamed: R12.2, R13.1, U2.6
unnamed: R14.1, U1.20
unnamed: R16.1, R18.2, R19.1, U1.7
unnamed: R17.2, R18.1, RT1.2
unnamed: R20.2, U3.3
unnamed: R24.2, U4.4
unnamed: R25.2, U4.10
unnamed: R26.2, U4.7
unnamed: R36.2, R37.1, R38.2, U7.4
unnamed: R38.1, U7.5
unnamed: R39.2, U7.2
unnamed: U1.9, U1.10, U1.14
unnamed: U2.7, U2.8
unnamed: U7.6, U9.2, U9.4
unnamed: U7.10, U8.2, U8.4
unnamed: U8.5, U8.6, U8.7, U8.8
unnamed: U9.5, U9.6, U9.7, U9.8
PWM: J2.12, R23.2, R26.1
V7.5V: C7.1, D2.1, J2.2, J2.19, L2.2, R12.1
V7.5V_EN: J2.16, R8.1, U2.5
VBATT: C9.1, D4.1, F1.2, J2.3, U7.7, U9.3
VIN_12V: C15.1, J1.1, J1.2, R1.1, R6.1, R9.1, R10.1, R27.2, R36.1, R39.1, U1.23, U1.25, U7.9, U8.1
V_MAIN: C4.1, C13.1, J2.17, J6.1, J7.1, R20.1, R21.1, U2.2, U3.5, U7.8, U8.3, U9.1
nMOTOR-FAULT-A: J2.8, U4.5
nMOTOR-FAULT-B: J2.9, U4.9

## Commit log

2020-10-24 Initial upload of V2.7 design to OpenVent Repo.
    [Battery_Charger.sch, FPGA_A.sch, FPGA_B.sch, Microcontroller.sch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]
2020-10-25 Still had some text cleanups to do plus fixed a couple of minor circuit issues.
    [Battery_Charger.sch, FPGA_A.sch, FPGA_B.sch, Microcontroller.sch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]
2020-10-29 Rick added system block diagram to the top level sheet and changed some file names.
    [FPGA.sch, JTAG.sch, OpenVent.sch]
2020-10-30 Updating my local branch, wip Friday 10/30/20. Got sucked into fixing up the libraries for the BOM...
    [Battery_Charger.sch, FPGA.sch, Microcontroller.sch, Motor_Driver.sch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]
2020-10-31 Continuing on with library updates. Started to fix up the USB interfaces.
    [Battery_Charger.sch, FPGA.sch, JTAG.sch, Microcontroller.sch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]
2020-11-01 Put USB to JTAG page together, first cut.
    [JTAG.sch, Microcontroller.sch]
2020-11-05 Tweaked some issues on the battery charger page.
    [Battery_Charger.sch, Motor_Driver.sch]
2020-11-09 Added in 8 RGB LEDs for the UI.
    [FPGA.sch, JTAG.sch]
2020-11-11 Battery Charger page mostly finished, might want to think about what to do with the battery charging current signal (it's analog).
    [Battery_Charger.sch, FPGA.sch, Motor_Driver.sch, Power_Supplies.sch]
2020-11-16 Split the design into two boards, main controller board and a power supply board.
    [Battery_Charger.sch, FPGA.sch, JTAG.sch, Microcontroller.sch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]
2020-11-17 Sorted out the interconnect between power supply and main boards.
    [Battery_Charger.sch, FPGA.sch, JTAG.sch, Microcontroller.sch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]
2020-11-19 First cut at a placement study for the power board.
    [Motor_Driver.sch, OV_Power.kicad_pcb, OV_Power.sch, PowerSupply.sch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]
2020-11-23 New board outline and power connector added. Still need definition of connector for microswitches and schematic.
    [Motor_Driver.sch, OV_Power.kicad_pcb, PowerSupply.sch]
2020-11-23 Successful merge of Shrookie's changes to main
    [FPGA.sch, FPGA_JTAG_SPECIAL.sch, FPGA_JTAG_SPECIAL_PWR.sch, JTAG.sch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]
2020-11-27 Getting on with the placement of the power board, functional blocks are all grouped together, just need to fit them all in now.
    [Battery_Charger.sch, Motor_Driver.sch, OV_Power.kicad_pcb]
2020-12-01 Continuing to refine both the schemo and placement for the power supply board. I think we have all the connectors we need now...
    [OV_Power.kicad_pcb, OV_Power.sch, PowerSupply.sch]
2020-12-02 Finished off a tentative placement for the power board.
    [OV_Power.kicad_pcb]
2020-12-07 Added two connectors for cooling fans, re-jigged the motor current sensing circuit a bit, still needs a bit of work there.
    [Motor_Driver.sch, OV_Power.kicad_pcb, OV_Power.sch, PowerSupply.sch]
2020-12-09 Finished schemo and placement of power supply board, then resolved interconnects with the main board.
    [FPGA_JTAG_SPECIAL_PWR.sch, Motor_Driver.sch, OV_Power.kicad_pcb, OV_Power.sch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]
2020-12-12 First cut at complete routing for the power board. Still need DRC checking and final fettling of the BOM and silkscreens before going to press.
    [Motor_Driver.sch, OV_Power.kicad_pcb, OV_Power.sch, PowerSupply.sch]
2020-12-17 Some cleanups of the silkscreen on the power board...
    [FPGA.sch, OV_Power.kicad_pcb]
2020-12-17 First cut at a 3D rendering of the board. Not too many missing models...
    [FPGA.sch, FPGA_JTAG_SPECIAL_PWR.sch, OV_Power.kicad_pcb]
2020-12-19 Changed the power input jack to a shielded version of the same part. Note that the same footprint can be used with either shielded or unshielded versions.
    [OV_Power.kicad_pcb, PowerSupply.sch]
2020-12-21 Changes some stuff
    [FPGA.sch, FPGA_JTAG_SPECIAL_PWR.sch]
2020-12-21 Went through the whole circuit and made a note of what needs changing
    [Buzzer_LEDs.sch, FPGA.sch, FPGA_JTAG_SPECIAL_PWR.sch, JTAG.sch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]
2020-12-21 Re-jigging the pcb outline for the power board...
    [OV_Power.kicad_pcb]
2020-12-24 Tentative placement (again...) for power board, also added a ferrite part for Shrouk to the main library.
    [Motor_Driver.sch, OV_Power.kicad_pcb]
2020-12-24 Detailed description of changes below:
    Sheet 2:
    WD protection: 33ohm resistor in series in each line and then on the side between the resistor and micro put the ESD diode
    ferrite beads and ESD prot on JP2
    NRST PULLED UP TO 3V3Always on
    VDD USB to 3V3
    Sheet 6:
    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
    [FPGA.sch, FPGA_JTAG_SPECIAL_PWR.sch, Microcontroller.sch]
2020-12-27 Finally getting on with board routing, in TWO layers. Warning, some things changed on the 20 pin interconnect.
    [Motor_Driver.sch, OV_Power.kicad_pcb, PowerSupply.sch]
2020-12-29 Power board routing is finished in 2 layers, but pcb outline is apparently changing yet again...
    [OV_Power.kicad_pcb, OV_Power.sch]
2020-12-29 TLV75512 ON fpga jtag special PWR sheet 7 Changed Q2 on Buzzer LEDs sheet 8 from N type to P type
    TLV75512 ON fpga jtag special PWR sheet 7
    Changed Q2 on Buzzer LEDs sheet 8 from N type to P type
    [Buzzer_LEDs.sch, FPGA.sch, FPGA_JTAG_SPECIAL_PWR.sch, Sensors.sch]
2020-12-30 The power board is finished, output generated. Still need to make a sensible bill of materials but that is probably best done from the schematic at this stage.
    [OV_Power-B_Cu.gbr, OV_Power-B_Mask.gbr, OV_Power-Edge_Cuts.gbr, OV_Power-F_Cu.gbr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]
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2020-12-31 Minor change to power board schematic, fix a stray no connect.
    [Motor_Driver.sch]
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2021-01-07 Changing connectors again, also fixed a library fubar...
    [Motor_Driver.sch, OV_Power.kicad_pcb, OV_Power.sch, OpenVent.kicad_pcb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]
2021-01-07 Added 3 pin JST 10amp connector for the battery. Now all we have to worry about is connecting the wiring harness to the battery correctly...
    [OV_Power.kicad_pcb, OV_Power.sch]
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2021-01-18 Corrected power ON/OFF control circuit signal labels
    [Power_Supplies.sch]
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2021-02-08 Laura fixing her file structure
    [FPGA_copy.sch]
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2021-02-09 Corrected several mistakes in the FPGA symbol, fixed up the FPGA page a little bit. NOTE: some pin assignments changed position to make reading the schematic easier and to clarify some of the pin fun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
    [FPGA.sch, FPGA_JTAG_SPECIAL_PWR.sch]
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2021-02-10 More fixing up of the FPGA symbols, lashed up the sigma delta A/D converter circuitry. Fixed up the LCD page. Two displays, two separate enables needed here folks. FPGA I/O banks power supplies' need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
    [FPGA.sch, FPGA_JTAG_SPECIAL_PWR.sch, LCD_FPGA.sch, Microcontroller.sch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]
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2021-02-15 Sensor page edited, notes added and connectors swapped to 4way SMD
    [Sensors.sch]
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2021-03-17 Header symbol has been replaced
    [JTAG.sch]
2021-03-17 Revert "update ad_conv"
    This reverts commit 2591c2734f3c7e5145f1228234b79b44e77147b9.
    [AD_conv.sch]
2021-03-17 Revert "Revert "update ad_conv""
    This reverts commit c371a4cca322dd3fb3e49e6407b5727743ee6e3b.
    [AD_conv.sch]
2021-03-17 Revert "8-way buffer for ADC changed to 74ACT244PW"
    This reverts commit 929fdbb6ff0d88cacb7b87749e61dcb260247704.
    [AD_conv.sch]
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2021-03-17 Removed second Vref from U9 on ADC page, replaced with additional 8th input, G
    [AD_conv.sch, FPGA.sch]
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2021-03-22 PWM and SPI_FPGA_CS pins swapped on MCU
    [JTAG.sch, Microcontroller.sch]
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2021-03-29 Replaced Mini USB connector on MCU sheet with Micro-B USB. Added VUSB label to power supply 3V3 always on circuit.
    [Microcontroller.sch, Power_Supplies.sch]
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2021-03-29 Swapped in Rick's front sheet. Note that this changed the sheet order, which appears to be automatically assigned and cannot be edited back to what it was manually
    [OpenVent.sch]
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2021-03-31 Current limiting on regulators and pin swapping between power and main board
    [AD_conv.sch, OpenVent.sch, PowerSupply.sch, Power_Supplies.sch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]
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2021-04-06 Note added to Power_Supplies for Rick to try to fix Power_Supplies page issue
    [FPGA.sch, Power_Supplies.sch]
2021-04-07 Replaced front sheet, added Speaker_Driver sheet
    New front sheet provided by Rick on 02/04/2021 with re-ordered pages and addition of Speaker_Driver
    [AD_conv.sch, FPGA.sch, JTAG.sch, Microcontroller.sch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]
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2021-04-12 Update UI.sch
    keypad buffer replaced
    [UI.sch]
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2021-04-21 Output BOM. Swapped some resistors to match text value
    R68 was 12k symbol but 4k7 text, changed to 4k7 symbol. R71, R69, R70, R73, R67, R65 were 12k symbol but 10k text, swapped to 10 symbol.
    [JTAG.sch]
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2021-05-10 Updated BLM31KN102SN1L library part and replaced pre-existing one on Power Supplies sheet
    [Power_Supplies.sch]
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2021-05-11 Update Power_Supplies.sch
    7.5V input signals corrected for regulator
    [Power_Supplies.sch]
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2021-05-23 Beginning the process of design review, fixed a couple howlers.
    [FPGA.sch, JTAG.sch, Microcontroller.sch, Power_Supplies.sch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]
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2021-07-12 Update JTAG.sch
    Q4, Q5 replaced
    [JTAG.sch]
2021-07-12 Update FPGA.sch
    Q2, Q3 replaced
    [FPGA.sch]
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
